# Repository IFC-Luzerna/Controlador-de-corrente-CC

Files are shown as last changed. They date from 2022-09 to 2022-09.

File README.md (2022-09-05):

# Controlador de corrente CC

Projeto de um controlador de corrente CC 5A desenvolvido pelos técnicos do IFC - Campus Luzerna para ser utilizado nas disciplinas relacionadas com máquinas e acionamentos elétricos. O objetivo é utilizar esse controlador para acionar um freio acoplado diretamente a um motor de indução trifásico, criando assim um simulador de cargas. Assim, os alunos podem observar as diferentes características de acionamentos quando utilizados em diferentes situações.

Agradecimentos especiais vão para os colaboradores Clecio Jung, Darlan Klotz, Dionathan Luan de Vargas e Marcos Fiorin.

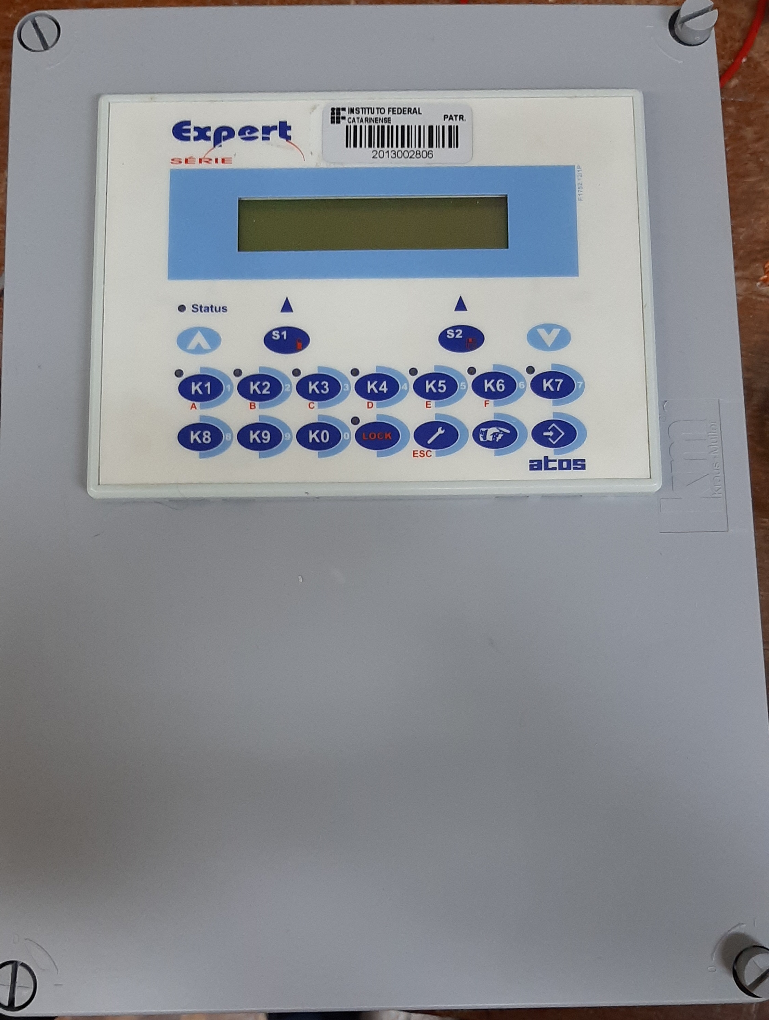
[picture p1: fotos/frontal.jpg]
frontal

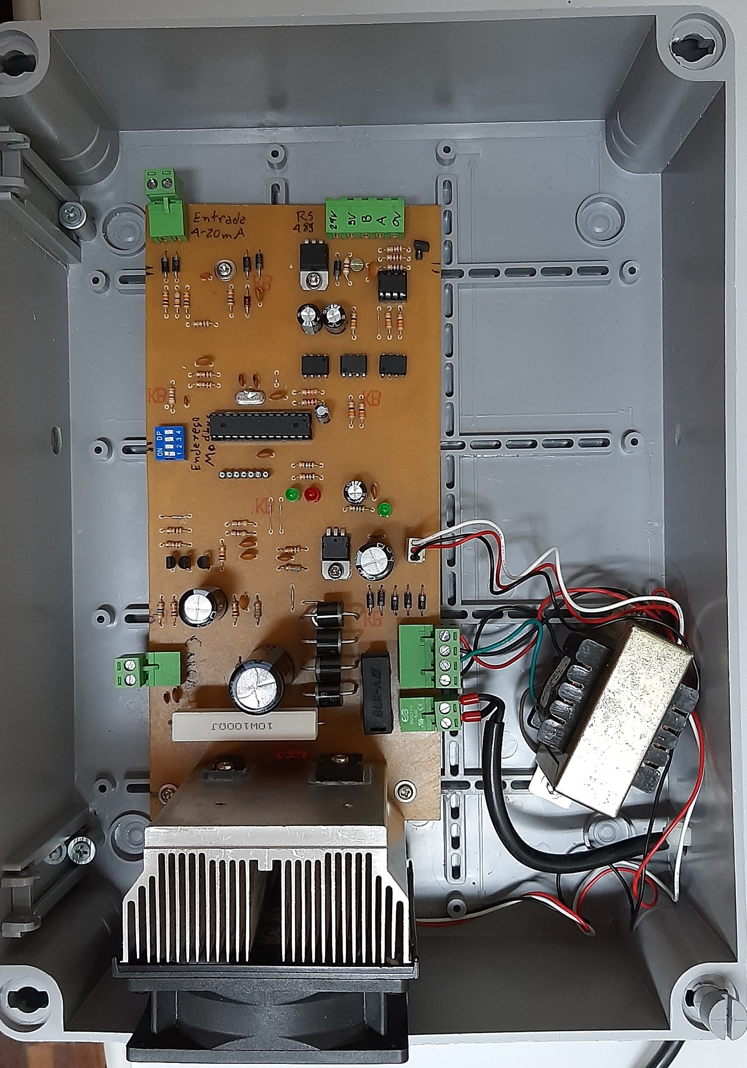
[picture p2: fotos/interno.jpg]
interno

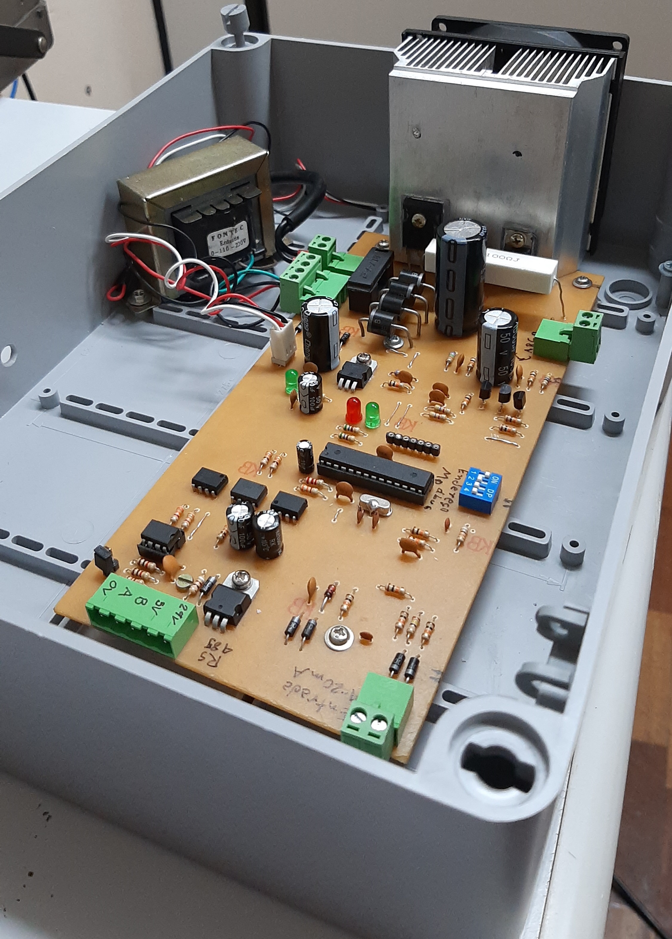
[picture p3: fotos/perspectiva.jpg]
perspectiva


## Descritivo do projeto

Características do controlador de corrente:

- Hardware eletrônico desenvolvido no software Autodesk Eagle versão 9.6.2, e o projeto pode ser adquirido na pasta [circuito eletrônico](./circuito%20eletronico/);

- Firmware do microcontrolador ([Atmega8](https://ww1.microchip.com/downloads/en/DeviceDoc/Atmel-2486-8-bit-AVR-microcontroller-ATmega8_L_datasheet.pdf)) desenvolvido no software Microchip Studio versão 7.0, e os arquivos podem ser adquiridos na pasta [firmware](./firmware/);

- O controlador pode operar como escravo em rede Modbus RS-485:
    - O circuito de comunicação RS-485 é isolado e precisa de alimentação independente (5V ou 24V contínuos);
    - Código utilizado para implementar a comunicação provem da biblioteca [ModBus_RTU_Drivers](https://github.com/RicardoKers/ModBus_RTU_Drivers);
    - Endereço configurável através de chaves dip switch de quatro posições. O valor desejado para o endereço deve ser convertido para binário primeiro, e depois as chaves devem ser configuradas de acordo. Os endereços possíveis estão entre 0 e 15. O endereço 0 não corresponde a um endereço Modbus válido, e portanto, a comunicação Modbus é desabilitada, e o setpoint do controlador passa a ser definido pela entrada analógica 4-20mA (maiores detalhes abaixo).
    - A comunicação dispõe de três registradores de leitura e escrita (funções 3, 6 e 16 do protocolo Modbus):

| Endereço | Range      | Descrição |
| -------- | ---------- | --------- |
| 0        | 200 - 1000 | Valor amostrado da entrada analógica 4-20mA. O valor desse registrador é proporcional à corrente na entrada analógica, sendo que o valor 200 indica corrente de 4mA, e o valor 1000 indica corrente de 20mA. Caso a leitura nesse registrador indique valores inferiores a 200, a entrada está desconectada ou o cabo rompido. Escrever algum valor nesse registrador não terá efeito algum. |
| 1        | 0 - 1000   | Valor amostrado da corrente de carga. O valor desse registrador é proporcional à corrente na carga, sendo que o valor 0 indica 0A, e o valor 1000 indica 5A. Escrever algum valor nesse registrador não terá efeito algum. |
| 2        | 0 - 1000   | Referência (setpoint) de corrente. Segue o mesmo range de unidades do parâmetro anterior. Valor a ser escrito pelo mestre Modbus usado (caso esteja usando comunicação RS-485) |

- O controlador pode ainda receber a referência de corrente (setpoint) a partir da entrada analógica 4-20mA:
    - Para ativar essa opção, deve-se configurar as dip switch de configuração do endereço modbus no valor 0 (todas desabilitadas). Nesse caso, 4mA na entrada representam setpoint de 0A, e 20mA corresponde a referência de 5A. Valores inferiores a 4mA na entrada representam erro (provavelmente o cabo está rompido ou a entrada desconectada), e nesse caso o controlador desliga a carga e o led vermelho liga, indicando um erro;
    - O circuito da entrada analógica é isolado, não necesssita de alimentação independente e o sentido da corrente é arbitrario (funciona do mesmo jeito se a corrente na entrada analógica for positiva ou negativa);

- Quando o led vermelho na placa de circuito eletrônico estiver ligado, um erro ocorreu. Até o momento, apenas um erro é reportado:
    - Quando o setpoint é informado pela entrada analogica e o valor amostrado nessa entrada é inferior a 4mA (provavelmente o cabo está rompido ou a entrada desconectada);

- Na pasta [scada](./scada/) temos uma aplicação desktop simplista desenvolvida no software Elipse E3 (necessário instalá-lo para rodar a aplicação), onde a comunicação com o controlador já está implementada;

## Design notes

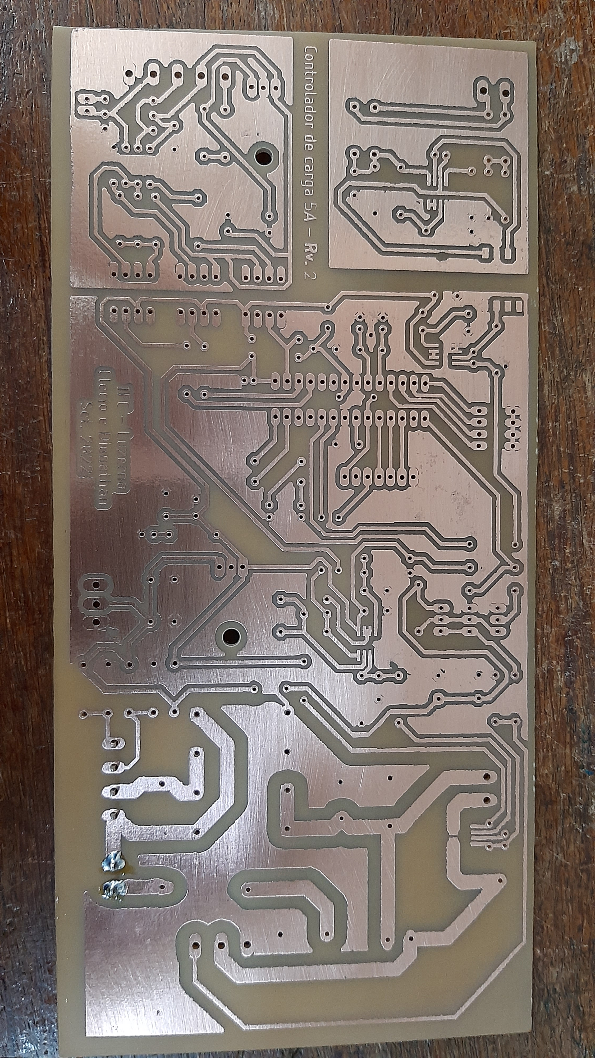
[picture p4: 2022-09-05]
fotos/pci.jpg

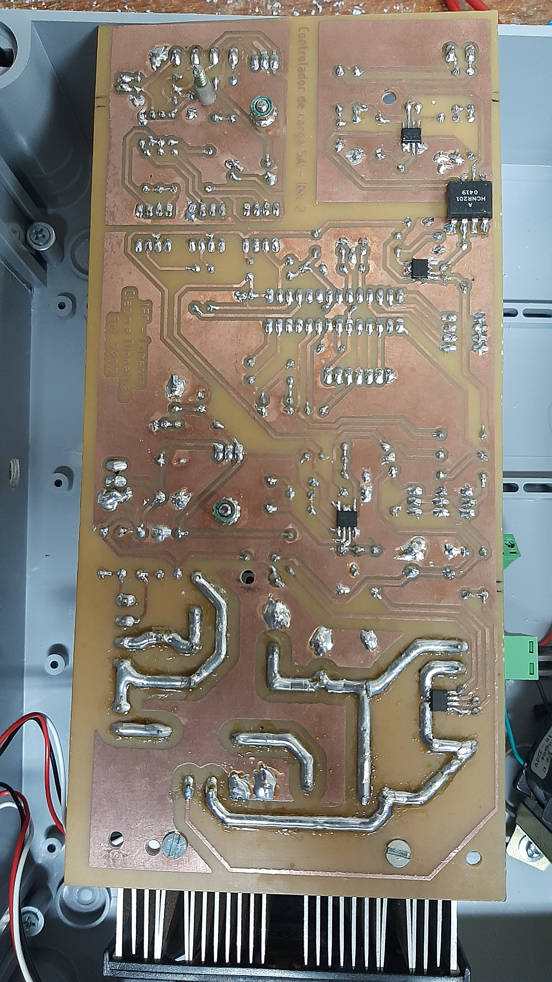
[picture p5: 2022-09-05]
fotos/pci_baixo.jpg

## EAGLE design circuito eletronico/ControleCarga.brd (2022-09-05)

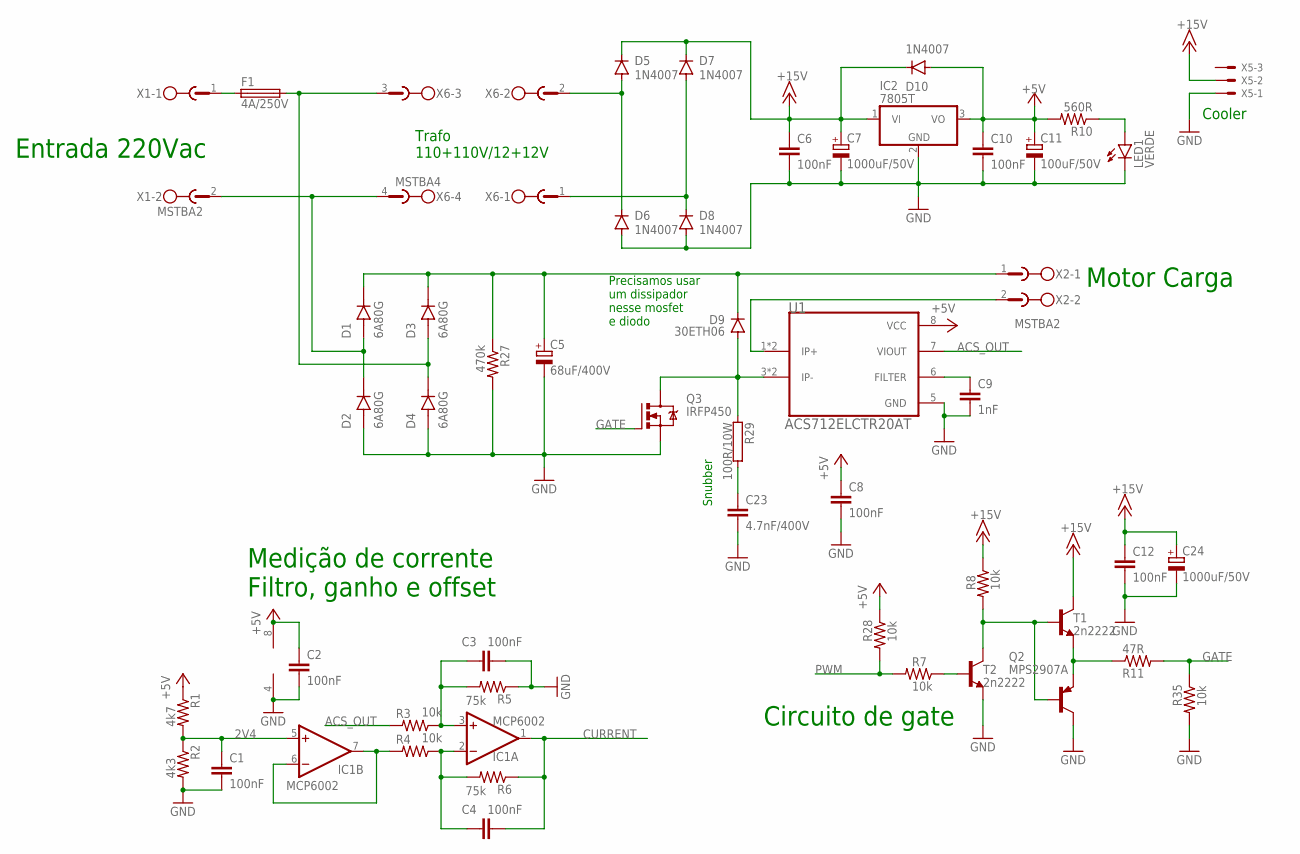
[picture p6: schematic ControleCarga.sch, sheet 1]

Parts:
C1, C2, C3, C4, C6, C8, C10, C12: 100nF; C050-025X075
C5: 68uF/400V; E7,5-18
C7, C24: 1000uF/50V; E5-13
C9: 1nF; C025-024X044
C11: 100uF/50V; E3,5-8
C23: 4.7nF/400V; C102-043X133
D1, D2, D3, D4: 6A80G; DIOAD1950W125L885D700
D5, D6, D7, D8, D10: 1N4007; DO41-10
D9: 30ETH06; TO220ACS
F1: 4A/250V; SH22
IC1: MCP6002; SO08
IC2: 7805T; TO220H
LED1: VERDE; LED5MM
Q2: MPS2907A; TO92-CBE
Q3: IRFP450; TO247BV
R1: 4k7; 0207/10
R2: 4k3; 0207/10
R3, R4, R7, R8, R28, R35: 10k; 0207/10
R5, R6: 75k; 0207/10
R10: 560R; 0207/10
R11: 47R; 0207/10
R27: 470k; 0207/10
R29: 100R/10W; KH216-8
T1, T2: 2n2222; TO92-EBC
U1: ACS712ELCTR20AT; SOIC127P600X175-8N
X1, X2: MSTBA2
X5: KK-156-3
X6: MSTBA4

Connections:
2V4: C1.1, IC1.5 (+IN), R1.2, R2.1
+5V: C2.1, C8.1, C10.1, C11.+, D10.A, IC1.8 (V+), IC2.3 (VO), R1.1, R10.2, R28.1, U1.8 (VCC); also elsewhere on the board
+15V: C6.1, C7.+, C12.1, C24.+, D5.C, D7.C, D10.C, IC2.1 (VI), R8.1, T1.C, X5.2
ACS_OUT: R3.2, U1.7 (VIOUT)
CURRENT: C4.2, IC1.1 (OUT), R6.1; also elsewhere on the board
GATE: Q3.G, R11.2, R35.1
GND: C1.2, C2.2, C3.2, C5.-, C6.2, C7.-, C8.2, C9.2, C10.2, C11.-, C12.2, C23.2, C24.-, D2.A, D4.A, D6.A, D8.A, IC1.4 (V-), IC2.2 (GND), LED1.K (C), Q2.C, Q3.S, R2.2, R5.1, R27.2, R35.2, T2.E, U1.5 (GND), X5.1; also elsewhere on the board
unnamed: D7.A, D8.C, X6.1
unnamed: C23.1, R29.2
unnamed: Q2.E, R11.1, T1.E
unnamed: LED1.A, R10.1
unnamed: D3.A, D4.C (K), F1.2, X6.3
unnamed: D1.A, D2.C (K), X1.2, X6.4
unnamed: U1.1 (IP+), U1.2 (IP+), X2.2
unnamed: D9.A, Q3.D, R29.1, U1.3 (IP-), U1.4 (IP-)
unnamed: C5.+, D1.C (K), D3.C (K), D9.C, R27.1, X2.1
unnamed: C9.1, U1.6 (FILTER)
unnamed: IC1.6 (-IN), IC1.7 (OUT), R4.2
unnamed: C4.1, IC1.2 (-IN), R4.1, R6.2
unnamed: C3.1, IC1.3 (+IN), R3.1, R5.2
unnamed: F1.1, X1.1
unnamed: R7.1, T2.B
unnamed: D5.A, D6.C, X6.2
unnamed: Q2.B, R8.2, T1.B, T2.C
PWM: R7.2, R28.2; also elsewhere on the board

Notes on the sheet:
Entrada 220Vac
Medição de corrente Filtro, ganho e offset
Motor Carga
Circuito de gate
Precisamos usar um dissipador nesse mosfet e diodo
Trafo 110+110V/12+12V
Snubber
Cooler

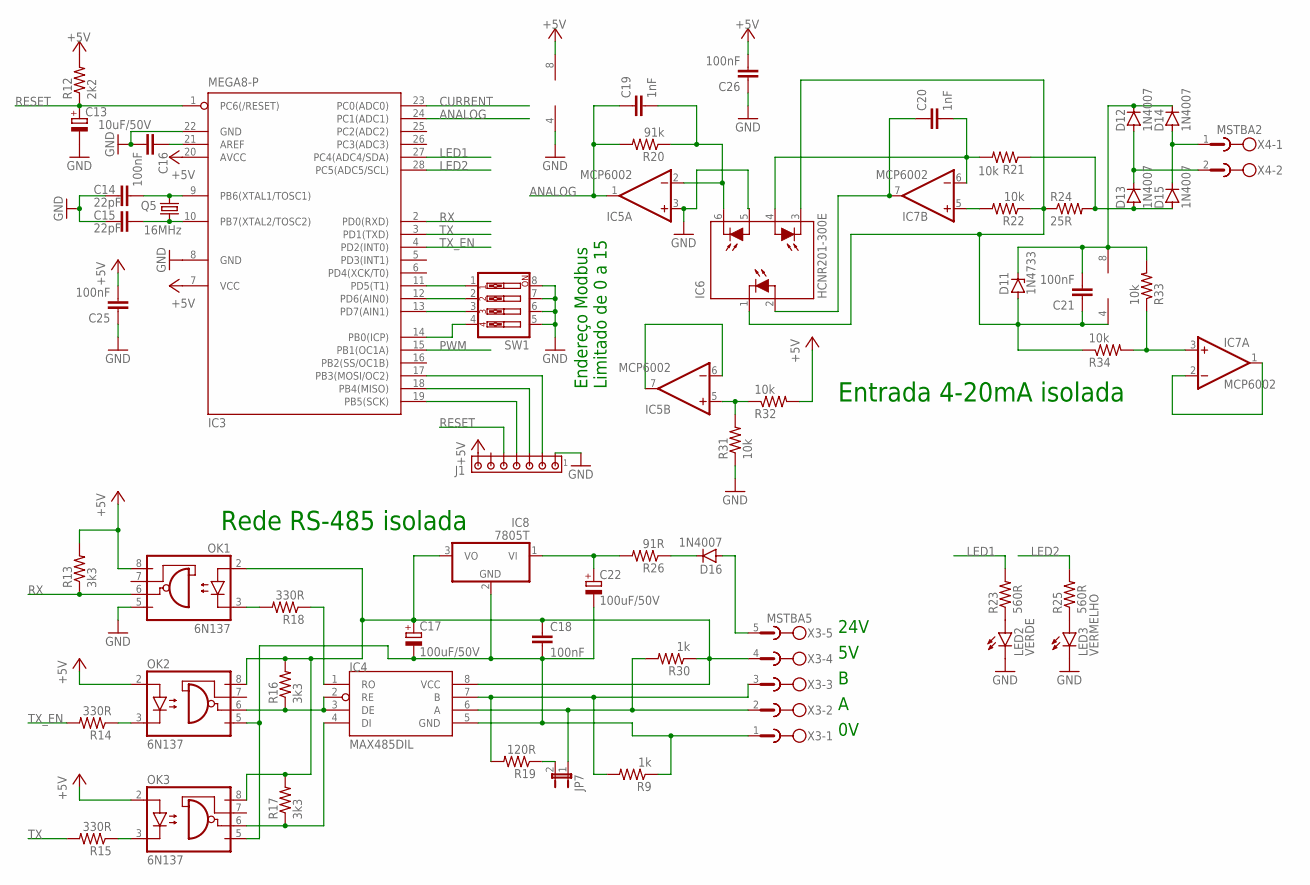
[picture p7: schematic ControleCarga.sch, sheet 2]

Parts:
C13: 10uF/50V; E2-5
C14, C15: 22pF; C025-024X044
C16, C18, C21, C25, C26: 100nF; C050-025X075
C17, C22: 100uF/50V; E3,5-8
C19, C20: 1nF; C025-024X044
D11: 1N4733; DO41Z10
D12, D13, D14, D15, D16: 1N4007; DO41-10
IC3: MEGA8-P; DIL28-3
IC4: MAX485DIL; DIL08
IC5, IC7: MCP6002; SO08
IC6: HCNR201-300E; DIP8-400
IC8: 7805T; TO220H
J1: MTA07-100; 10X07MTA
JP7: JP1E; JP1
LED2: VERDE; LED5MM
LED3: VERMELHO; LED5MM
OK1, OK2, OK3: 6N137; DIL08
Q5: 16MHz; HC49/S
R9, R30: 1k; 0207/10
R12: 2k2; 0207/10
R13, R16, R17: 3k3; 0207/10
R14, R15, R18: 330R; 0207/10
R19: 120R; 0207/10
R20: 91k; 0207/10
R21, R22, R31, R32, R33, R34: 10k; 0207/10
R23, R25: 560R; 0207/10
R24: 25R; 0207/10
R26: 91R; 0207/10
SW1: SW_DIP-4; EDG-04
X3: MSTBA5
X4: MSTBA2

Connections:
0V: C17.-, C18.2, C22.-, IC4.5 (GND), IC8.2 (GND), OK2.5 (GND), OK3.5 (GND), R9.1, X3.1
+5V: C25.2, C26.2, IC3.7 (VCC), IC3.20 (AVCC), IC5.8 (V+), J1.7, OK1.8 (VCC), OK2.2 (A), OK3.2 (A), R12.2, R13.2, R32.2; also elsewhere on the board
ANALOG: C19.1, IC3.24 (PC1(ADC1)), IC5.1 (OUT), R20.2
CURRENT: IC3.23 (PC0(ADC0)); also elsewhere on the board
GND: C13.-, C14.2, C15.2, C16.2, C25.1, C26.1, IC3.8 (GND), IC3.22 (GND), IC5.3 (+IN), IC5.4 (V-), IC6.5 (A2), J1.1, LED2.K (C), LED3.K (C), OK1.5 (GND), R31.1, SW1.5, SW1.6, SW1.7, SW1.8; also elsewhere on the board
GNDISO: C21.1, D11.A, IC6.1 (C), IC6.3 (C1), IC7.4 (V-), R22.1, R24.1, R34.1
LED1: IC3.27 (PC4(ADC4/SDA)), R23.2
LED2: IC3.28 (PC5(ADC5/SCL)), R25.2
unnamed: C16.1, IC3.21 (AREF)
unnamed: IC4.2 (RE), IC4.3 (DE), OK2.6 (VO), R16.1
unnamed: D14.A, D15.C, X4.1
unnamed: LED2.A, R23.1
unnamed: IC3.14 (PB0(ICP)), SW1.4
unnamed: IC3.13 (PD7(AIN1)), SW1.3
unnamed: IC3.12 (PD6(AIN0)), SW1.2
unnamed: IC3.11 (PD5(T1)), SW1.1
unnamed: LED3.A, R25.1
unnamed: C21.2, D11.C, D12.C, D14.C, IC7.8 (V+), R33.2
unnamed: IC4.7 (B), R9.2, R19.2, X3.3
unnamed: IC4.6 (A), JP7.1, R30.2, X3.2
unnamed: IC4.4 (DI), OK3.6 (VO), R17.1
unnamed: OK1.3 (C), R18.2
unnamed: IC4.1 (RO), R18.1
unnamed: OK2.3 (C), R14.1
unnamed: OK3.3 (C), R15.1
unnamed: IC3.19 (PB5(SCK)), J1.4
unnamed: JP7.2, R19.1
unnamed: C19.2, IC5.2 (-IN), IC6.6 (C2), R20.1
unnamed: C22.+, IC8.1 (VI), R26.2
unnamed: IC5.6 (-IN), IC5.7 (OUT)
unnamed: IC7.1 (OUT), IC7.2 (-IN)
unnamed: C20.1, IC6.2 (A), IC7.7 (OUT)
unnamed: IC7.5 (+IN), R22.2
unnamed: D13.A, D15.A, R21.1, R24.2
unnamed: C20.2, IC6.4 (A1), IC7.6 (-IN), R21.2
unnamed: IC3.18 (PB4(MISO)), J1.3
unnamed: C17.+, C18.1, IC4.8 (VCC), IC8.3 (VO), OK1.2 (A), OK2.8 (VCC), OK3.8 (VCC), R16.2, R17.2, R30.1, X3.4
unnamed: IC3.17 (PB3(MOSI/OC2)), J1.2
unnamed: D16.A, X3.5
unnamed: D12.A, D13.C, X4.2
unnamed: C14.1, IC3.9 (PB6(XTAL1/TOSC1)), Q5.2
unnamed: C15.1, IC3.10 (PB7(XTAL2/TOSC2)), Q5.1
unnamed: D16.C, R26.1
unnamed: IC5.5 (+IN), R31.2, R32.1
unnamed: IC7.3 (+IN), R33.1, R34.2
PWM: IC3.15 (PB1(OC1A)); also elsewhere on the board
RESET: C13.+, IC3.1 (PC6(/RESET)), J1.5, R12.1
RX: IC3.2 (PD0(RXD)), OK1.6 (VO), R13.1
TX: IC3.3 (PD1(TXD)), R15.2
TX_EN: IC3.4 (PD2(INT0)), R14.2

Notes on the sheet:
Rede RS-485 isolada
Entrada 4-20mA isolada
Endereço Modbus Limitado de 0 a 15
24V

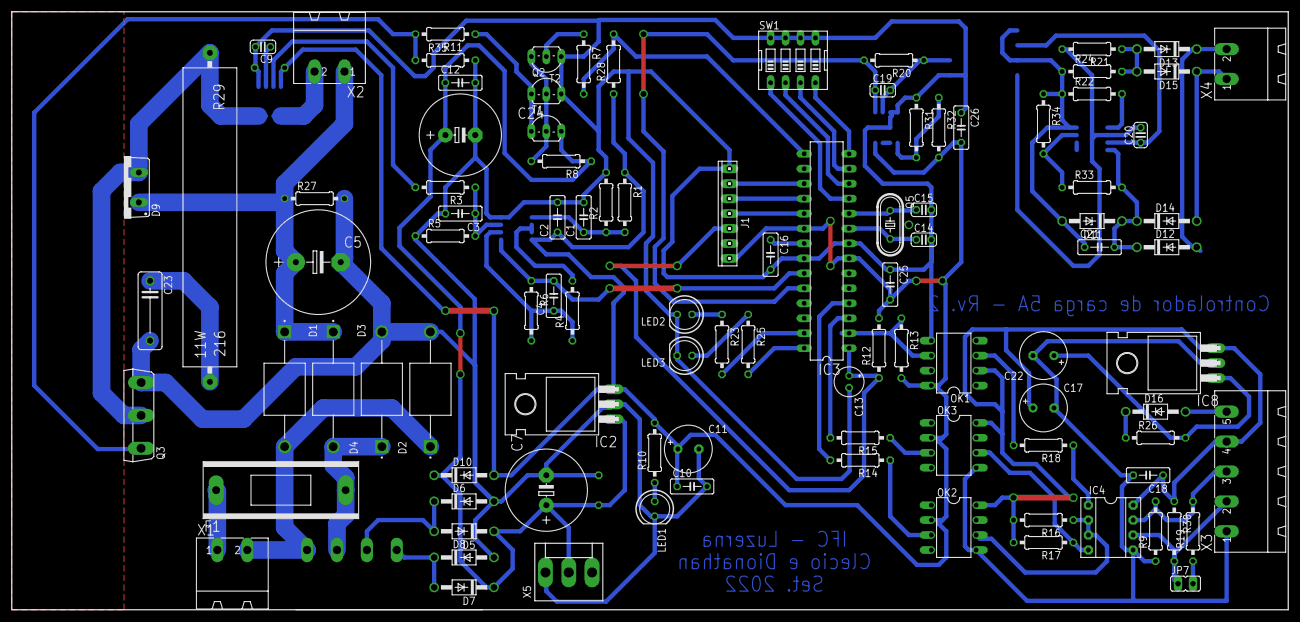
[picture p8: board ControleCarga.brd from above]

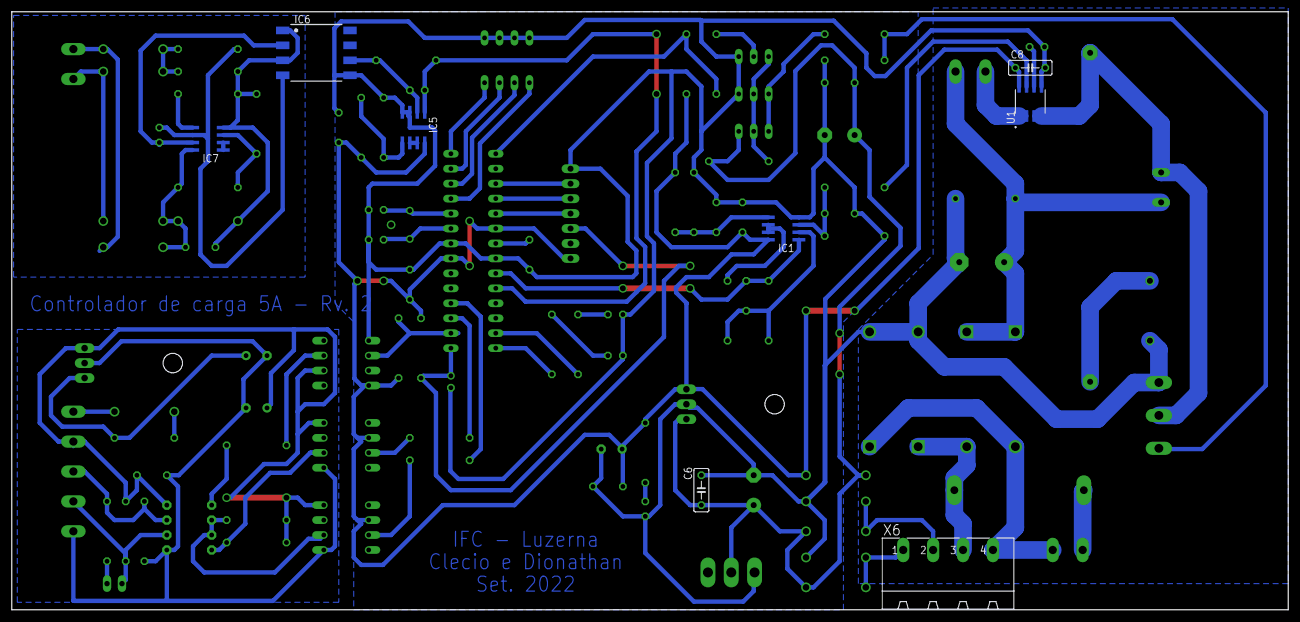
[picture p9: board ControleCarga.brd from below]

Board: 2 copper layers, 216.8 x 101.6 mm, 107 parts (8 on the bottom side), 71 nets.

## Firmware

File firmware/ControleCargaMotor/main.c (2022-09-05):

//-------------------------------------------------------------------------------------------------------
#define F_CPU 16000000UL

#include <avr/io.h>
#include <avr/interrupt.h>
#include <util/delay.h>
#include "ModBusSlave.h"

//-------------------------------------------------------------------------------------------------------
// Constants

// LED test
#define SET_GREEN_LED()		(PORTC  |= (1<<PC4))
#define CLEAR_GREEN_LED()	(PORTC  &= ~(1<<PC4))
#define TOOGLE_GREEN_LED()	(PORTC  ^= (1<<PC4))
#define SET_RED_LED()		(PORTC  |= (1<<PC5))
#define CLEAR_RED_LED()		(PORTC  &= ~(1<<PC5))
#define TOOGLE_RED_LED()	(PORTC  ^= (1<<PC5))

// Dip Switch
#define DIP_SWITCH()		((uint16_t)((((~PIND) & 0xF0)) >> 4))

// ajustes das entradas analógicas
#define ANALOG_INPUT_GAIN	((uint32_t)1074)
#define ANALOG_INPUT_OFFSET ((uint32_t)3769)
#define CURRENT_GAIN		((int32_t)1311)
#define CURRENT_OFFSET		((int32_t)-45462)

// Máximos valores para o PWM e setpoint
#define PWM_MAX					800
#define PWM_LIMIT				180
#define SETPOINT_MAX			1000

// Parametros da entrada analógica
#define ANALOG_INPUT_TOO_LOW	150
#define ANALOG_INPUT_MIN		200
#define ANALOG_INPUT_MAX		1000

// Modo de controle de corrente (open or closed loop)
#define CLOSED_LOOP				1

// Controller adjust
#define GAIN_K1					200
#define GAIN_K2					190

//-------------------------------------------------------------------------------------------------------
// Global variables

/*	entrada analógica isolada 4-20mA
	range: 200-1000
	se o valor for < 200, a corrente é inferior a 4mA
	e provavelmente o cabo está rompido
*/
volatile uint16_t analog_input = 0;
/*	medição de corrente na carga 0-5A
	range: 0-1000
*/
volatile uint16_t current = 0;
/*	setpoint para controle de corrente
	range: 0-1000
*/
volatile uint16_t setpoint = 0;

//-------------------------------------------------------------------------------------------------------
// Run PI control

struct PI {
	int16_t previousError;
	int32_t controlSignal;
};

void piClear(struct PI *pi) {
	pi->previousError = 0;
	pi->controlSignal = 0;
}

struct PI piCurrent;

uint16_t piControl(struct PI *pi, uint16_t setPoint, uint16_t feedBack)
{
	int16_t error = setPoint - feedBack;
	pi->controlSignal += GAIN_K1 * error - GAIN_K2 * pi->previousError;
	pi->previousError = error;
	
	if (pi->controlSignal >= (int32_t)PWM_LIMIT*1000) {
		pi->controlSignal = (int32_t)PWM_LIMIT*1000;
	} else if (pi->controlSignal < 0) {
		pi->controlSignal = 0;
	}

	return (uint16_t)(pi->controlSignal/1000);
}

static inline void controle(void) {
	// operando com setpoint enviado pela entrada analógica
	if (ModBus.end_modbus == 0) {
		if (analog_input < ANALOG_INPUT_MIN) {
			setpoint  = 0;
		} else if (analog_input > ANALOG_INPUT_MAX) {
			setpoint = SETPOINT_MAX;
		} else {
			uint32_t sp32 = ((uint32_t)SETPOINT_MAX)*((uint32_t)(analog_input - ANALOG_INPUT_MIN));
			setpoint = (uint16_t) (sp32/((uint32_t)(ANALOG_INPUT_MAX - ANALOG_INPUT_MIN)));
		}
	}
	
	#if CLOSED_LOOP
		OCR1A = piControl(&piCurrent, setpoint, current);
	#else // open loop
		OCR1A = setpoint;
	#endif
}

static inline uint16_t dip_switch(void) {
	const uint16_t bit0 = (PIND&(1<<PD5)) ? 0:1;
	const uint16_t bit1 = (PIND&(1<<PD6)) ? 0:1;
	const uint16_t bit2 = (PIND&(1<<PD7)) ? 0:1;
	const uint16_t bit3 = (PINB&(1<<PB0)) ? 0:1;
	return ((bit3<<3)|(bit2<<2)|(bit1<<1)|(bit0<<0));
}

//-------------------------------------------------------------------------------------------------------
// ADC - Entradas Analógicas

// O ADC do Atmega8 não é muito bom. Segundo o datasheet, não deveriamos usar uma frequencia maior do que 200kHz,
// o que restringe bastante a frequência de operação. Além disso, o ADC consome 13 ciclos para fazer a medição,
// o que implica na frequência de amostragem máxima de 200/13 = 15,38kHz (medindo apenas um canal).
// E acima de tudo isso, não existe um meio para medir continuamente varios canais, temos de tratar isso no 
// codigo da interupção, o que torna a frequencia de amostragem variavel com o codigo gravado no processador.
ISR(ADC_vect)
{
	cli();
	// fs = 4.54kHz, T = 220us (medido experimentalmente com o osciloscópio)
	uint32_t adc = ADCW;
	
	// Le próximo canal
	ADMUX ^= (1<<MUX0);
	ADCSRA |= (1<<ADSC);
	
	if (ADMUX & (1<<MUX0)) {
		const int32_t current32 = (CURRENT_GAIN * (int32_t)adc + CURRENT_OFFSET)/1000;
		current = current32 > 0 ? (uint16_t)(current32) : 0;
		controle();
	} else {
		analog_input = (uint16_t)((ANALOG_INPUT_GAIN * (uint32_t)adc + ANALOG_INPUT_OFFSET)/1000);
	}
	sei();
}

//-------------------------------------------------------------------------------------------------------
int main(void)
{
	// Leds
	DDRC |= (1<<DDC4) | (1<<DDC5);
	// Dip Switch - Liga os resistores de pull-up
	PORTD |= (1<<PD7)|(1<<PD6)|(1<<PD5);
	PORTB |= (1<<PB0);
	
	//-----------------------------------
	// ADC - Entradas Analógicas
	// Frequencia de Amostragem = 4.8kHz (medição de dois canais em sequência)
	ADMUX = (1<<REFS0);
	// Prescaler = /128, conversion cycles = 13, f = 9.6kHz, T = 200us
	ADCSRA = (1<<ADEN)|(1<<ADIE)|(1<<ADPS2)|(1<<ADPS1)|(1<<ADPS0);
	// Inicia nova conversão
	ADCSRA |= (1<<ADSC);

	//-----------------------------------
	// Timer 1 - PWM
	PORTB |= (1<<PB1);
	TCNT1 = 0;
	OCR1A = 0;
	ICR1 = PWM_MAX; // Freq = 10kHz
	TCCR1A = (1 << COM1A1)|(1 << COM1A0)|(1 << WGM11); // Set OC1A on Compare Match and clear at BOTTOM
	TCCR1B = (1 << WGM13)|(1 << WGM12)|(1 << CS10); // Mode 14, Fast PWM, overflow on ICR1, set prescaler to 1
	DDRB |= (1<<DDB1);
	
	usart_init(); // inicia a comunicação serial utilizada na ModBus
	ModBusReset(); // prepara para receber a transmissão
	
	// Inicializa variaveis internas do controlador
	piClear(&piCurrent);
	
	// Enable interrupts
	sei();
	
	uint32_t counter = 0;
	
	// Main loop
	while (1)
	{
		counter++;
		if (counter >= 50000) {
			counter = 0;
			TOOGLE_GREEN_LED();
		}
		
		if (ModBus.status == aguardando || ModBus.end_modbus == 0) {
			uint8_t novo_endereco = dip_switch();
			if (ModBus.end_modbus != novo_endereco) {
				setpoint = 0; // reseta o setpoint para desligar o sistema
				piClear(&piCurrent);
				ModBus.data_reg[2] = 0;
				ModBus.end_modbus = novo_endereco;
			}
		}
		
		if (ModBus.end_modbus != 0)	{
			if (ModBus.status == processando) {
				ModBusProcess(); // inicia o processamento do pacote
			}
			ModBus.data_reg[0] = analog_input;
			ModBus.data_reg[1] = current;
			if (ModBus.data_reg[2] < SETPOINT_MAX) {
				setpoint = ModBus.data_reg[2];
			} else {
				setpoint = SETPOINT_MAX;
			}
		}
		
		if ((ModBus.end_modbus == 0) && (analog_input < ANALOG_INPUT_TOO_LOW)) {
			// liga led vermelho para indicar que a entrada analógica está recebendo menos de 4mA
			SET_RED_LED();
		} else {
			CLEAR_RED_LED();
		}
	}
}
//-------------------------------------------------------------------------------------------------------

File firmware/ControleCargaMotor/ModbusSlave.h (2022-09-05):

/*
 *		ModBusSlave.h
 *
 *		Versão: 03-2022
 *      Author: Kerschbaumer (com pequenas modificações feitas por Clecio Jung)
 *
 *  Funções implementadas:
 *
 *  	Read Holding Registers (FC=03)
 *  	Preset Single Register (FC=06)
 *  	Preset Multiple Registers (FC=16)
 */

// Configuração ModBus
#define endereco_modbus 1 // endereço inicial da modbus, pode ser mudado depois
#define num_reg_words_modbus 3 // número de registradores (words) usados na modbus (variável data_word) funções 3 e 16
#define tam_buff_recep 255
#define tam_buff_trans 255
#define TxDelay 100 // TX Delay ms
// final Configuração ModBus

// configuração da serial
#define USART_BAUDRATE 19200 // taxa de transmissão desejada
#define BAUD_PRESCALE ((F_CPU / (USART_BAUDRATE * (long)16))-1) //calcula o valor do prescaler da usart
// fim da configuração da serial

// configuração do pino do driver RS485
#define ModBusTxEnablePort PORTD
#define ModBusTxEnablePin PD2
#define ModBusTxEnableDDR DDRD

#define ModBusRxEnable() ModBusTxEnablePort &= ~(1<<ModBusTxEnablePin) // Habilita a recepção do driver RS485
#define ModBusTxEnable() ModBusTxEnablePort |= (1<<ModBusTxEnablePin) // Habilita a transmissão do driver RS485

unsigned int ModBusTimerCont = 1;
unsigned int ModBusTimerInterval = 0;

struct mb
{
	enum e_status {aguardando, recebendo, processando, ignorando, iniciandoTransmisao, transmitindo} status;
	uint8_t end_modbus; // armazena o endereço na modbus
	uint16_t rxsize; // tamanho do pacote na recepção
	uint16_t txsize; // tamanho do pacote na transmissão
	uint8_t rxbuf[tam_buff_recep]; // buffer de recepção
	uint8_t txbuf[tam_buff_trans]; // buffer de transmissão
	uint8_t funcao;
	uint16_t data_reg[num_reg_words_modbus]; // dados de words a serem transmitidos e recebidos pela modbus
	uint16_t rxpt; // ponteiro para o buffer de recepçao, necessario em algumas arquiteturas
	uint16_t txpt; // ponteiro para o buffer de transmissão, necessario em algumas arquiteturas
} ModBus;

// Liga o temporizador usado na modBus com o intervalor ajustado para 1ms
// Ajustar para o clock utilizado
void inicia_timer_1ms()
{
	OCR2 = 250;			// Ajusta o valor de comparação do timer 2
	TCNT2 = 0;			// Zera a contagem do timer 2
	TCCR2 = (1<<CS22);	// habilita o clock do timer 2 com prescaller /64
	TIMSK |= (1<<OCIE2);	// habilita a interrupção do timer 2
}

// Liga o temporizador usado na modBus, deve ficar antes do #include "ModBusSlave.h"
void liga_timer_modbus(unsigned char t_ms)
{
	cli();
	ModBusTimerCont=0;
	ModBusTimerInterval=t_ms;
	inicia_timer_1ms();
	sei();
}

//	desliga o temporizador usado na modBus
#define desliga_timer_modbus() (TCCR2 = 0) // desliga o timer da modbus

// reseta o temporizador usado na modBus
#define reset_timer_modbus() (TCNT2 = 0) // reseta o timer da modbus

uint16_t CRC16Table256(uint16_t i) // gera tabela de crc
{
	uint16_t crc,c,j;
	crc = 0;
	c   = (uint16_t) i;
	for (j=0; j<8; j++)
	{
		if ( (crc ^ c) & 0x0001 ) crc = ( crc >> 1 ) ^ 0xA001;
		else crc =   crc >> 1;
		c = c >> 1;
    }
	return crc;
}

uint16_t update_crc_16(uint16_t crc, uint8_t c) // atualiza o valor do crc
{
	uint16_t tmp, short_c;
	short_c = 0x00ff & (uint16_t) c;
	tmp =  crc       ^ short_c;
	crc = (crc >> 8) ^ CRC16Table256((uint16_t) tmp & 0xff);
	return crc;
}

uint16_t CRC16(uint8_t *ptr,uint16_t npts) // calcula o crc de um vetor
{
	uint16_t crc;
	uint16_t i;
	crc=0xffff;// valor inicial para CRC16modbus
	for(i=0;i<npts;i++)
	{
		crc=update_crc_16(crc,(uint8_t) *(ptr+i));
    }
	return crc;
}

void ModBusReset()
{
	ModBusRxEnable();
	ModBus.rxsize=6;
	ModBus.end_modbus=endereco_modbus;
	ModBus.status=aguardando;
	ModBus.rxpt=0;
	ModBus.txpt=0;
}

void ModBusDefineFunction(uint8_t rchar)
{
	uint16_t tmp;
	if(rchar==3) //função 3 (identifica a função 3 do modbus)
	{
		ModBus.rxsize = 7; // prepara para receber 7 bytes conforme função 3
		ModBus.funcao=3;
		return;
	}
	if(rchar==6) //função 6 (identifica a função 6 do modbus)
	{
		ModBus.rxsize = 7; // prepara para receber 7 bytes conforme função 6
		ModBus.funcao=6;
		return;
	}
	if(rchar==16) //função 16 (identifica a função 16 do modbus)
	{
		tmp=(uint16_t)((ModBus.rxbuf[4]<<8)|ModBus.rxbuf[5]);
		ModBus.rxsize = 8+(tmp*2); // depende do número de registradores a ser alterados
		ModBus.funcao=16;
		return;
	}
	// função inválida, ignorando
	ModBus.status=ignorando;
	ModBus.rxsize = tam_buff_recep; // tamanho máximo	
}

void ModBusSendErrorMessage(uint8_t function, uint8_t code)
{
	uint16_t crc; // armazena o valor do crc do pacote
	ModBus.txbuf[0]=ModBus.end_modbus; // inicia o pacote de resposta com o endereço
	ModBus.txbuf[1]=function|0x80; // indica a função 1 na resposta com erro
	ModBus.txbuf[2]=code; // indica o número de registradores transmitidos em bytes
	crc=CRC16(ModBus.txbuf,3); // calcula o crc da resposta
	ModBus.txbuf[3]=(uint8_t)(crc&0x00ff); // monta 8 bits do crc para transmitir
	ModBus.txbuf[4]=(uint8_t)(crc>>8); // monta mais 8 bits do crc para transmitir
	ModBus.txsize=5; // armazena o tamanho do pacote para transmissão
	ModBus.status = iniciandoTransmisao; // atualiza o status para o main ativar o timer
	liga_timer_modbus(TxDelay);
}

void ModBusProcess()
{
	uint16_t crc; // armazena o valor do crc do pacote
	uint16_t temp; // variável para valores temporários
	uint16_t num_reg; // número de registradores que estão sendo lidos
	uint16_t cont_tx; // armazena o tamanho do pacote de transmissão
	uint16_t cont; // variável para contar os registradores transmitidos
	
	//verificar se é rxsize-1 ou rxsize-2 nas duas linhas a seguir
	crc=CRC16(ModBus.rxbuf,ModBus.rxsize-1); // calcula o crc do pacote
	if((uint8_t)(crc&0x00ff)==ModBus.rxbuf[ModBus.rxsize-1]&&(uint8_t)(crc>>8)==ModBus.rxbuf[ModBus.rxsize]) // testa se o crc é válido
	{
		if(ModBus.funcao==3) // se for a função 3
		{
			temp=(uint16_t)((ModBus.rxbuf[2]<<8)|ModBus.rxbuf[3]); //recebe o endereço dos registradores a serem lidos
			num_reg=(uint16_t)((ModBus.rxbuf[4]<<8)|ModBus.rxbuf[5]); // recebe a quantidade de registradores a serem lidos
			if((temp+num_reg-1)<num_reg_words_modbus) // verifica se é válido
			{
				ModBus.txbuf[0]=ModBus.end_modbus; // inicia o pacote de resposta com o endereço
				ModBus.txbuf[1]=3; // indica a função 3 na resposta
				ModBus.txbuf[2]=(uint8_t)(num_reg*2); // indica o número de registradores transmitidos em bytes
				cont_tx=3; // inicia o contador de tamanho do pacote de resposta
				for(cont=0; cont<num_reg; cont++) // conta os registradores enviados
				{
					ModBus.txbuf[cont_tx]=(uint8_t)((ModBus.data_reg[cont+temp])>>8); // envia os 8 bits mais altos do registrador
					cont_tx++; // incrementa o contador do tamanho da resposta
					ModBus.txbuf[cont_tx]=(uint8_t)((ModBus.data_reg[cont+temp])&0x00ff); // envia os 8 bits mais baixos do registrador
					cont_tx++; // incrementa o contador do tamanho da resposta
				}
				crc=CRC16(ModBus.txbuf,(uint16_t)((num_reg*2)+3)); // calcula o crc da resposta
				ModBus.txbuf[cont_tx]=(uint8_t)(crc&0x00ff); // monta 8 bits do crc para transmitir
				cont_tx++; // incrementa o contador do tamanho da resposta
				ModBus.txbuf[cont_tx]=(uint8_t)(crc>>8); // monta mais 8 bits do crc para transmitir
				cont_tx++; // incrementa o contador do tamanho da resposta
				ModBus.txsize=(uint8_t)(cont_tx); // armazena o tamanho do pacote para transmissão
				ModBus.status = iniciandoTransmisao; // atualiza o status para o main ativar o timer
				liga_timer_modbus(TxDelay);
			}
			else
			{
				ModBusSendErrorMessage(3, 2); // retorna erro de endereço ilegal
			}
		}
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
